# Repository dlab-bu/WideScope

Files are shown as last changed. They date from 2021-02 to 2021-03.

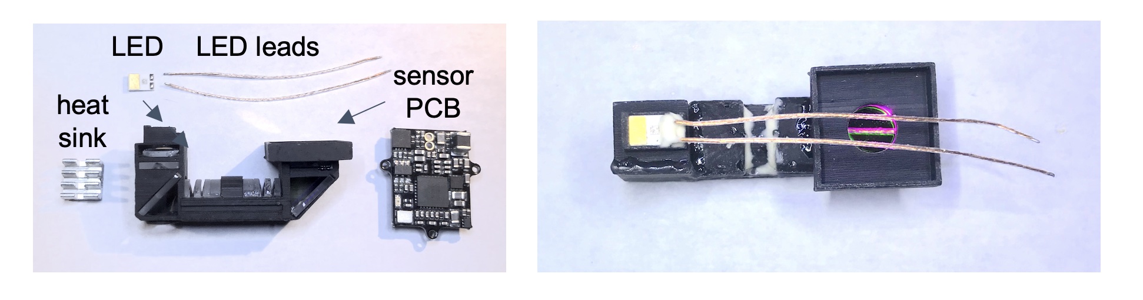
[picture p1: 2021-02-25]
zBuildGuideImages/f4_LED.jpg

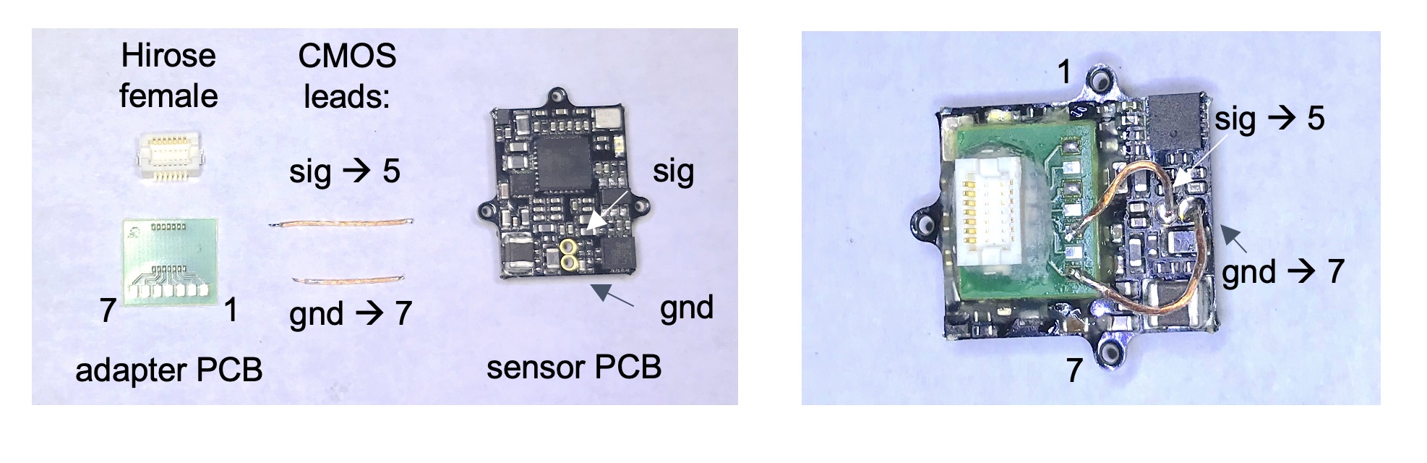
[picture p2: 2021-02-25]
zBuildGuideImages/f5_sensorPCB.jpg

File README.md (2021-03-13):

# WideScope - large-area, cellular-resolution imaging in behaving animals

This page provideas all component lists, print files, assembly instructions, and code for assembling a large-area miniscope.

### Overview

Miniaturized microscopes for head-mounted fluorescence imaging are powerful tools for visualizing neural activity during naturalistic behaviors, but the restricted field of view of first-generation ‘miniscopes’ can limit the size of neural populations accessible for imaging. This page describes a design for a miniaturized 'mesoscope' allowing cellular-resolution imaging over areas spanning several millimeters in freely moving mice. 

### Citation

The design and use of the scope is described in the following bioRxiv preprint:

Large-scale cellular-resolution imaging of neural activity in freely behaving mice.
D.P. Leman, I.A. Chen, K.A. Bolding, J. Tai, L.K. Wilmerding, H.J. Gritton, Y. Cohen, W.W. Yen, L.N. Perkins, W.A. Liberti III, K. Kilic, X. Han, A. Cruz-Martín, T.J. Gardner, T.M. Otchy, I.G. Davison.

doi: https://doi.org/10.1101/2021.01.15.426462 

### Components and assembly

The design is based on a 3-D printed housing combined with off-the-shelf optical components available from commercial suppliers. It can be implemented with different sensor options depending on experimental needs.

Files for 3D printing different housing configurations are above, and linked to here:.

https://github.com/dlab-bu/WideScope/tree/main/3D_Print_Files

A components list is above and linked to here:

https://docs.google.com/spreadsheets/d/1gIpmSVnjN3Ketk4CQQ4sIoGWy5cocQ0lN56zsxl2whk/edit#gid=0

An assembly guide is here:

https://github.com/dlab-bu/WideScope/wiki/WideScope-Assembly-Guide

Details for connector and cable options are here:

https://github.com/dlab-bu/WideScope/wiki/Cable-&-Interface-Assembly-Guide

MATLAB code for acquiring synchronized neural imaging data and behavioral video is here:

https://github.com/dlab-bu/WideScope/tree/main/Acquisition_Code

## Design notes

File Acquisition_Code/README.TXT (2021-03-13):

ACQUISITION CODE
________________

The MATLAB code here allows for synchronized acquisition of neural imaging data 
and behavioral video, with associated timestamps.

Imaging data can be captured by any software that recognizes the corresponding video sources.
Matlab will require the Image Acquisition toolbox installed, along with the 3rd party support packages:
UCLA sensor:    UVC / winvideo
Ximea sensor:   GenTL

Solid-state drives are highly recommended for streaming data to diskat typical frame rates.

The user interface is started by running:
fcnVidAcqV3_Main

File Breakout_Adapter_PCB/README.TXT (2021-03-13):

BREAKOUT ADAPTER PCB
____________________

We use lightweight Hirose connectors to interface between the miniscope 
and the image data and LED power cables.  The Hirose connectors in turn
are mounted on small breakout PCBs for ease of soldering.

The files here can be used to fabricate the PCB boards through 
commercial vendors.

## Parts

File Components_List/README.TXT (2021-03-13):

COMPONENTS LIST
_______________

The Excel sheet above contains information current as of Feb / 2021.

For the most current version, please see the online sheet at:
https://docs.google.com/spreadsheets/d/1gIpmSVnjN3Ketk4CQQ4sIoGWy5cocQ0lN56zsxl2whk/edit#gid=0

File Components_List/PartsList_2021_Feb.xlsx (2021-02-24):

This sheet is current as of Feb / 2021. Please see the online parts list for the most up-to-date version.
Component | # needed | Vendor | Part # | Website | Note
---- housing ----
Scope body and doors | 1 | N/A | N/A | N/A | Printed with FormLabs Form 2 / 3; black resin. Design file should match desired sensor type and aperture stop size.
Lens cover | 2 | N/A | N/A | N/A | Printed with FormLabs Form 2 / 3; black resin.
---- optics ----
imaging path lens, planoconvex 6 mm diam x 18 mm FL, coated | 6 | Edmund optics | 47-464 | https://www.edmundoptics.com/p/60mm-dia-x-180mm-fl-vis-0deg-coated-plano-convex-lens/7519/ | Antireflective coated for visible wavelengths.
image path lens, double-concave 6 mm diam x -12 mm FL, vis coated | 2 | Edmund optics | 48-693 | https://www.edmundoptics.com/p/6mm-dia-x12mm-fl-vis-0deg-coated-double-concave-lens/8948/ | Antireflective coated for visible wavelengths.
LED collimation lens, Half-Ball Lens, 3 mm | 1 | Edmund optics | 47-269 | https://www.edmundoptics.com/p/30mm-diameter-n-bk7-half-ball-lens/7289/
LED collimation lens, planoconvex 6 mm diam x 12 mm FL, vis coated | 1 | Edmund optics | 47-462 | https://www.edmundoptics.com/p/60mm-dia-x-120mm-fl-vis-0deg-coated-plano-convex-lens/7515/ | Antireflective coated for visible wavelengths.
dichroic mirror, 505 nm shortpass, 6 x 8.5 mm | 2 | Thorlabs | DMSP505R | https://www.thorlabs.com/thorproduct.cfm?partnumber=DMSP505R | Note: requires custom order for dicing to appropriate size.
excitation bandpass filter, 470 +/- 40 nm, 6.25 x 6.25 x 1 mm | 1 | Chroma | ET470/40x | https://www.chroma.com/products/parts/et470-40x | Note: requires custom order for dicing to appropriate size.
emission bandpass filter, 525 +/- 50 nm, 6.25 x 6.25 x 1mm | 1 | Chroma | ET525/50m | https://www.chroma.com/products/parts/et525-50m | Note: requires custom order for dicing to appropriate size.
---- excitation source and control ----
LED, blue high-power Luxeon Rebel | 1 | Digikey | LXML-PB02 | https://www.digikey.com/en/products/detail/lumileds/LXML-PB02/3961135
Heat sink | 1 | Adafruit | 1515 | https://www.adafruit.com/product/1515
BuckPuck LED supply / regulator | 1 | Digikey | 788-1109-ND | https://www.digikey.com/en/products/detail/leddynamics-inc/3021-D-E-700/3114435 | LED Dynamics 3021-D-E-700. Board-mount version; wired versions also available if preferred.
DAQ unit for software control of LED output | 1 | National Instruments | USB-6009 | https://www.ni.com/en-us/support/model.usb-6009.html | Any DAQ device supporting 0-5V analog output should work.
potentiometer for manual control of LED output | 1 | Mouser | 317-2090F-5K | https://www.mouser.com/ProductDetail/Alpha-Taiwan/RV09AF-40-20K-B5K?qs=gYx6oXzZQuvSFm4ihSuFBg%3D%3D | Any suitable 5K potentiometer should work.
miniature PCB breadboard |  | Adafruit | 571 | https://www.adafruit.com/product/571
---- image sensor options ----
low-resolution, high-speed: UCLA miniscope group CMOS | 1 | Labmaker | Miniscope - CMOS PCB | https://www.labmaker.org/products/cmos-pcb-miniscope | resolution 720 X 480 pixels, 4.8 µm pitch, frame rates up to 60 Hz
high-resolution, 5 MPix | 1 | Ximea | MU9PM-MBRD | https://www.ximea.com/en/products/application-specific-cameras/subminiature-cameras/mu9pm-mbrd | resolution 2592 x 1944, 2.2 µm pitch, frame rates approx. 5 Hz at full resolution
---- cabling and adapter ----
wire for on-scope LED and sensor connections |  | Cooner Wire | CZ1320
breakout PCB for connector interface | 1 | Advanced Circuits | N/A | N/A (custom order)
Hirose female 14-pin connector | 1 | Digikey | DF12E(3.0)-14DP-0.5V(81) | https://www.digikey.com/en/products/detail/hirose-electric-co-ltd/DF12E-3-0-14DP-0-5V-81/2170882
miniature coax cable | ~3 ft | Cooner Wire | CW2040-3650SR | https://www.coonerwire.com/mini-coax/ | Various size/AWG options will work; this option is robust but still thin and light for minimal behavioral impact
6-conductor flexible cable |  | Mogami |  |  | for use with Ximea high-resolution sensor

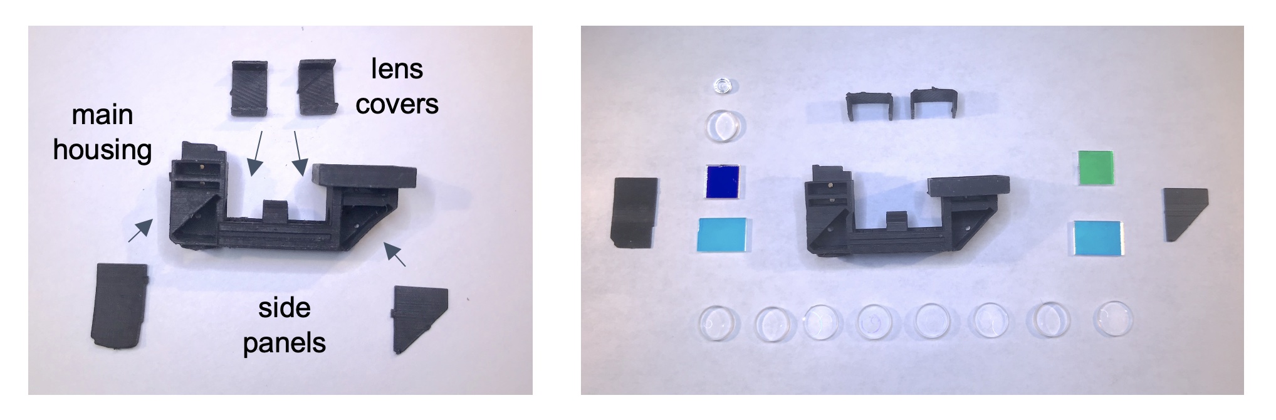
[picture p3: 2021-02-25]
zBuildGuideImages/f0_housing_components.jpg

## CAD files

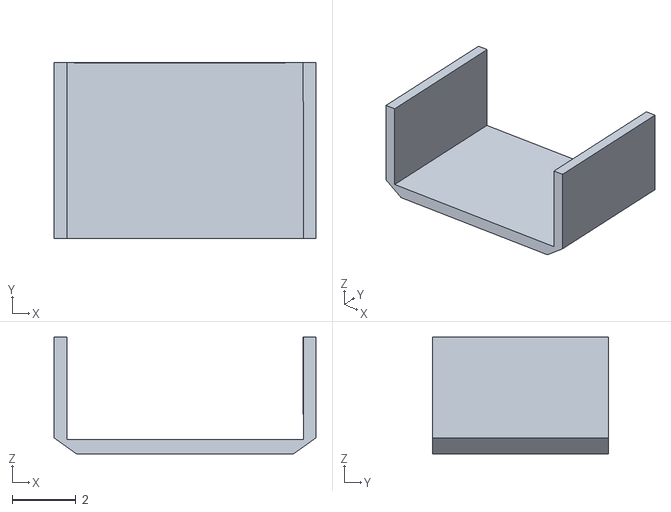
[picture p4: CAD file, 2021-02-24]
3D_Print_Files/housingV10_LensCover.stl
8.20 x 5.50 x 3.65

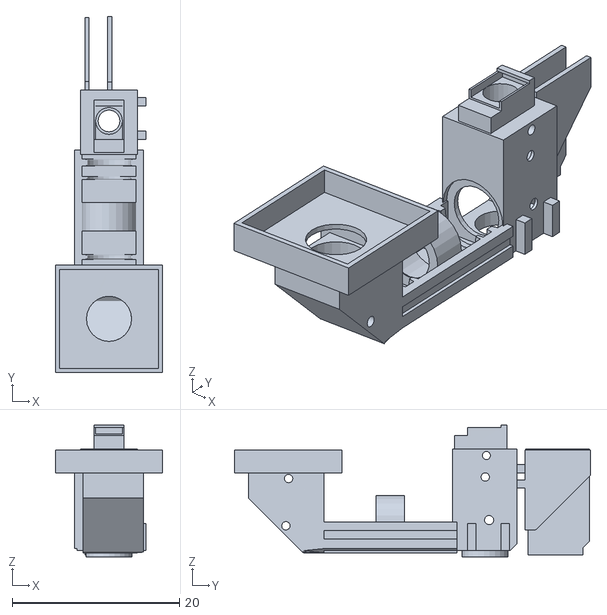
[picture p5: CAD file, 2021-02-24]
3D_Print_Files/housingV10_UCLA_apert45.stl
12.8 x 42.6 x 15.8

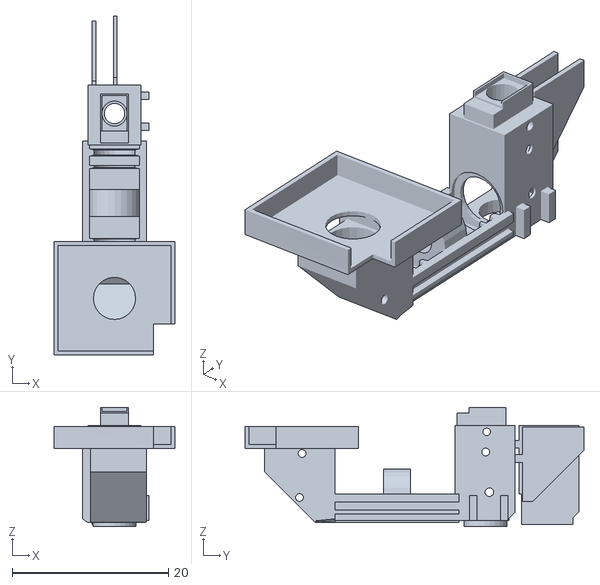
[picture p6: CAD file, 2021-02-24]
3D_Print_Files/housingV10_Ximea_apert30.stl
15.4 x 43.4 x 15.3

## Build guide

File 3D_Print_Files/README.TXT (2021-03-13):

3D PRINT FILES
______________

The .STL files here can be used to print the housing for the main scope body.   

The '_UCLA' and '_Ximea' versions are identical apart from the platform that holds the sensor chip.
Use the version that matches your hardware needs. 

The '_UCLA' version has a 4.5 mm aperture at the center of the optical path, 
giving maximal light collection but at the expense of reduced resolution at the FOV edges,
which has little impact given the pixel count for this sensor.

The '_Ximea' version has a 3.0 mm aperture at the center of the optical path, 
maintaining relatively efficient light collection while improving resolution at the FOV edges
for high-pixel-count cellular resolution imaging.

The single '_LensCover' file is used for both designs.
Two of these covers fit above the lens elements after they are loaded into the housing.  

We have successfully printed using Formlabs Form2 and Form3, using black resin.  
https://formlabs.com/3d-printers/form-2/
https://formlabs.com/3d-printers/form-3/

Washing and curing steps significantly impact the quality of the final scope.  
While not strictly necessary, the post-processing systems offered by FormLabs simplify these steps.
https://formlabs.com/post-processing/wash-cure/

Other printers and/or materials have not been tested.  
Key factors for other print systems will include print resolution, weight, and lightproofing/autofluorescence.

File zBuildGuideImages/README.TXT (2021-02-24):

This folder contains images linked to in the Wiki build guide.

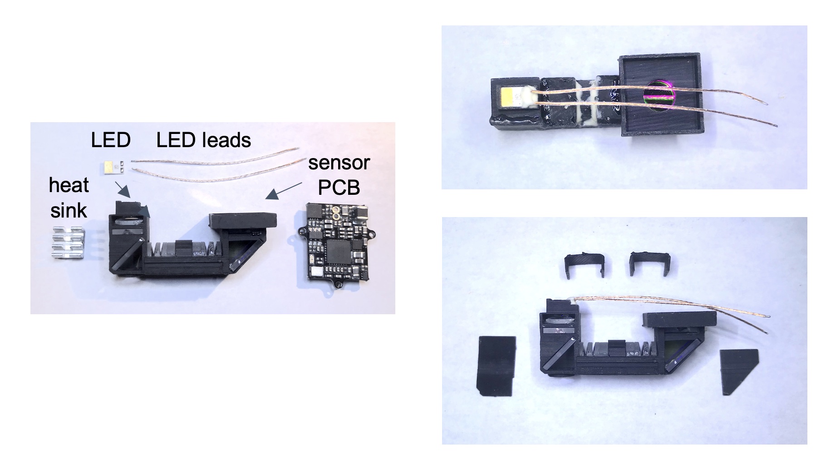
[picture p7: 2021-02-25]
zBuildGuideImages/f4_LED_panels.jpg

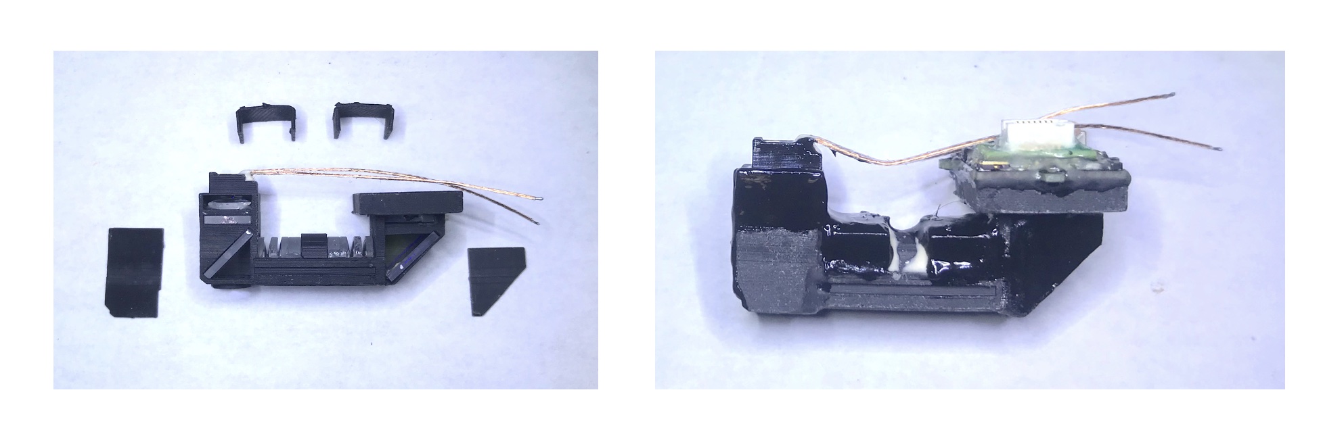
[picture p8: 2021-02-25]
zBuildGuideImages/f6_panels.jpg

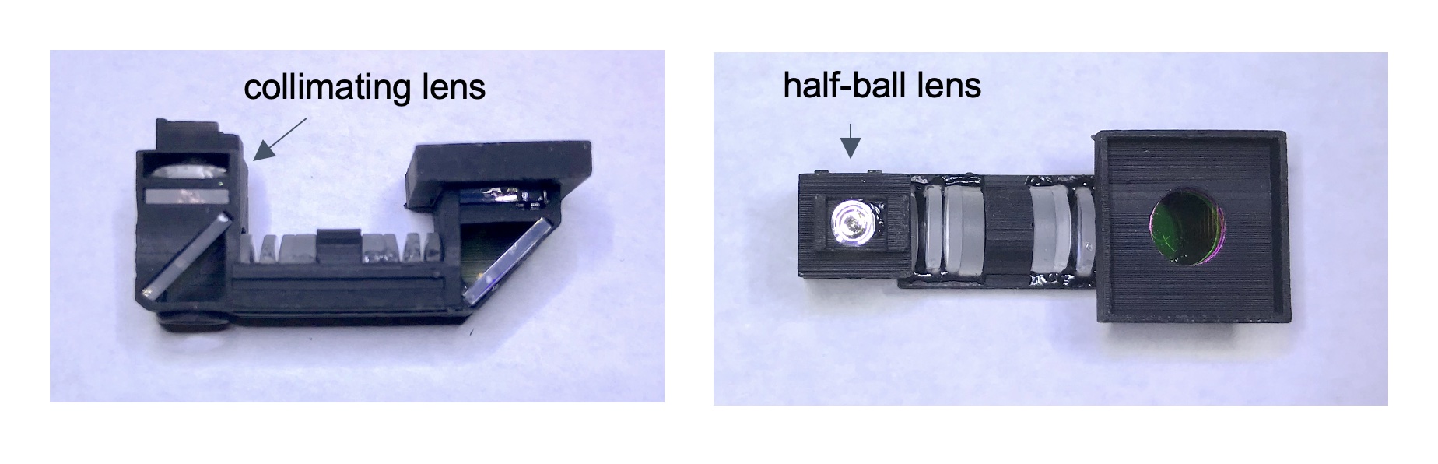
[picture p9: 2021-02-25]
zBuildGuideImages/f3_excitationPath.jpg
